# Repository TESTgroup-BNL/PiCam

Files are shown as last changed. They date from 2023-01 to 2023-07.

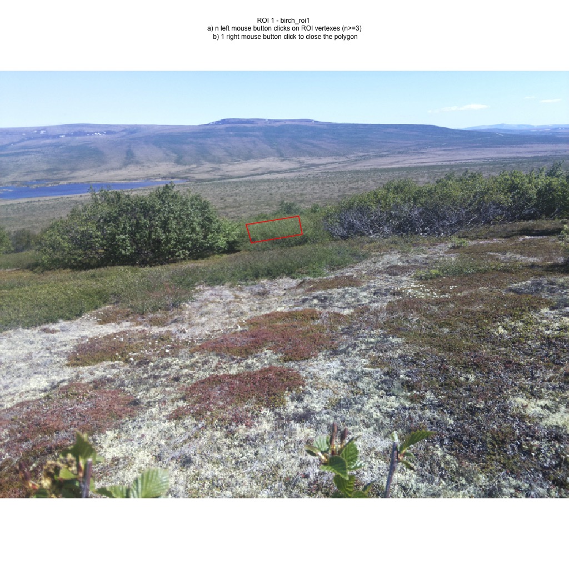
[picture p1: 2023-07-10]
Examples/Arctic_vegetation_phenology/pheno_results/roi/birch_roi1/spring/ROI1_birch_roi1.jpg

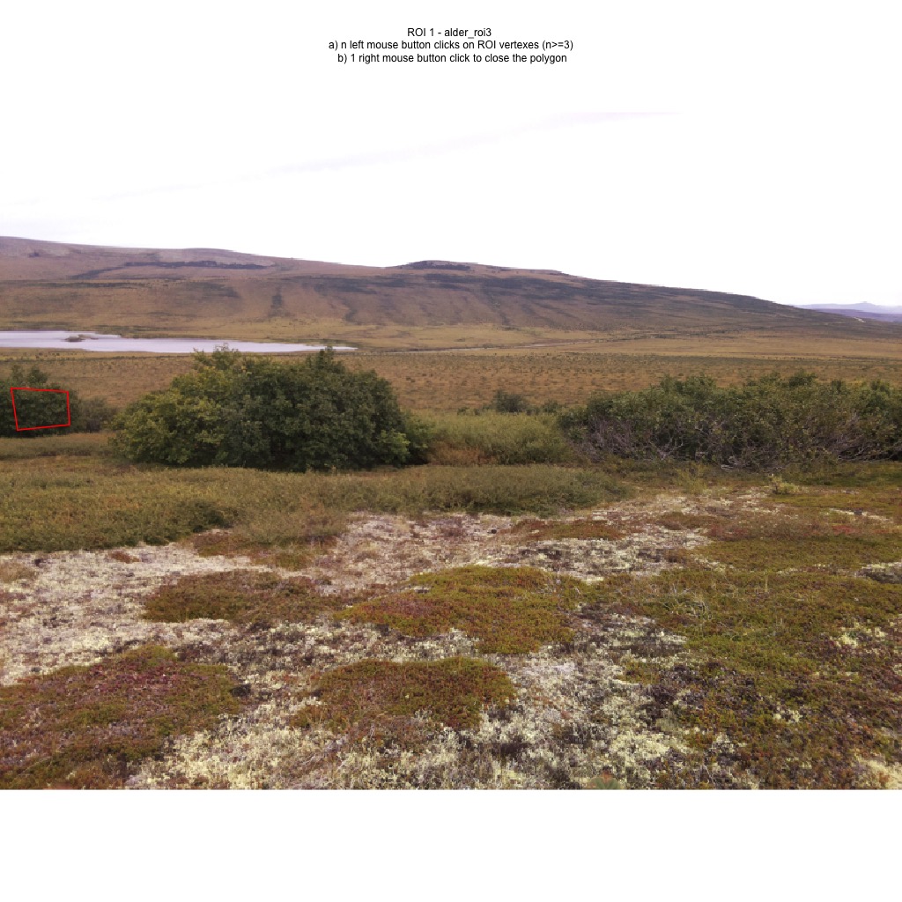
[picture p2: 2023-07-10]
Examples/Arctic_vegetation_phenology/pheno_results/roi/alder_roi3/fall/ROI1_alder_roi3.jpg

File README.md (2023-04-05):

### Source code citation: <br>


## Backgound
PiCAM is a custom-grade phenocam system designed by the [Terrestrial Ecosystem Science & Technology group](https://www.bnl.gov/envsci/testgroup/) at Brookhaven National Laboratory. The PiCAM has the advantage of being compact, low power cost, and lightweight, particularly suitable for Arctic environments. It was desinged to operate for at least a fiscal year (6 images per day) with three AA lithium batteries. Given its compact and light-weight feature, PiCAM can be deployed on small hosts (e.g., stakes), addressing the challenges of deploying heavy infrastructure commonly needed for commercial phenocams.

#### Below, we describe the parts, assemble, and basic operation of PiCAMs. Please also refer to Yang et al., (submitted to MEE) for more detailed technical description of the PiCAM and example applications in Arctic field sites. 

## 1. Parts for PiCAM
#### 2.1. Sensor Suite
* Camera (Raspberry Pi Camera v2; Raspberry Pi Foundation). Example source: https://www.raspberrypi.com/products/camera-module-v2/
* Camera cable (FFC Ribbon Cable; Generic). Example source: https://www.amazon.com/dp/B0716TB6X3/ref=twister_B08NTCX71W?_encoding=UTF8&psc=1
* GPS module (MINI GPS PA1010D STEMMA QT; Adafruit). Example source: https://www.digikey.com/en/products/detail/adafruit-industries-llc/4415/10709724
* GPS cable (FLEXIBLE QWIIC CABLE - 500MM; Sparkfun). Example source: https://www.digikey.com/en/products/detail/sparkfun-electronics/PRT-17257/13629026
#### 2.2. Central Control
* Supervisory controller (nrf52840; Nordic). Example source: https://www.digikey.com/en/products/detail/nordic-semiconductor-asa/NRF52840-DONGLE/9491124
* Camera controller (Raspberry Pi Zero; Raspberry Pi Foundation). Example source: https://www.raspberrypi.com/products/raspberry-pi-zero/
* Power Switch/Driver (TPS2080DR; Texas Instruments). Example source: https://www.digikey.com/en/products/detail/texas-instruments/TPS2080DR/1670863?s=N4IgTCBcDa4JwDYC0BmOKCsyCMSByAIiALoC%2BQA
#### 2.3. Power Supply
* Lithium Iron AA (Energizer; Part number: L91). Example source: https://www.energizer.com/batteries/energizer-ultimate-lithium-batteries
#### 2.4. Other Accessories
* Case (Flashlight; Fulton Industries). Example source: https://www.armynavysales.com/angle-head-flashlight-mx-991-u-me124-558.html
* Memory card (32GB Micro SD Card; Samsung). Users can choose the size depend on need
* SOIC-8 to DIP Breakout (BOB-13655; Sparkfun). Example source: https://www.digikey.com/en/products/detail/sparkfun-electronics/BOB-13655/5528943?s=N4IgTCBcDaIIwFYBsAOAtHOYDMaByAIiALoC%2BQA
* SWD Connector (10-pin 0.5mm; Samtec Inc.). Example source: https://www.digikey.com/en/products/detail/samtec-inc/SHF-105-01-F-D-SM/8410395

## 2. PiCAM Assembly, Programming, and Operation Guidance
A step-by-step instruction on how to assemble, program, and operate a PiCAM can be found at: https://github.com/TESTgroup-BNL/PiCam/wiki. Note that the assemble needed 3-D printed cases for housing the parts inside a Flashlight case. The design of these 3-D printed cases can be found at: https://github.com/TESTgroup-BNL/PiCam/tree/main/CAD. This guidance also include detailed instructions on how to program a PiCAM after assembly, as well how to operate a PiCAM using externel cell phone or latlop devices.

## Other Resources:
Adafruit nRF platform wrapper: https://github.com/dmpolukhin/Adafruit_nRF52_Arduino/tree/master/cores/nRF5

## Point of Contact:
Shawn Serbin: sserbin@bnl.gov Andrew Mcmahon: amcmahon@bnl.gov Daryl Yang: dediyang@bnl.gov Jeremiah Anderson: jeanderson@bnl.gov Wouter Hantson: wouter.hantson@umaine.edu

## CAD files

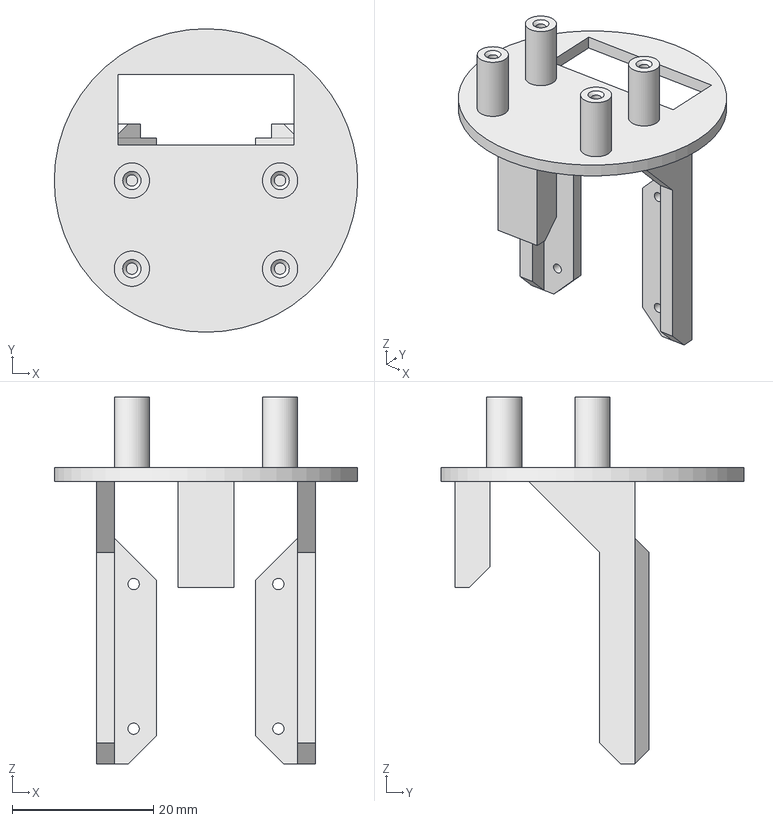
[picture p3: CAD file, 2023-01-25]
CAD/cam_holder_v2c.FCStd
43.0 x 43.0 x 52.0 mm

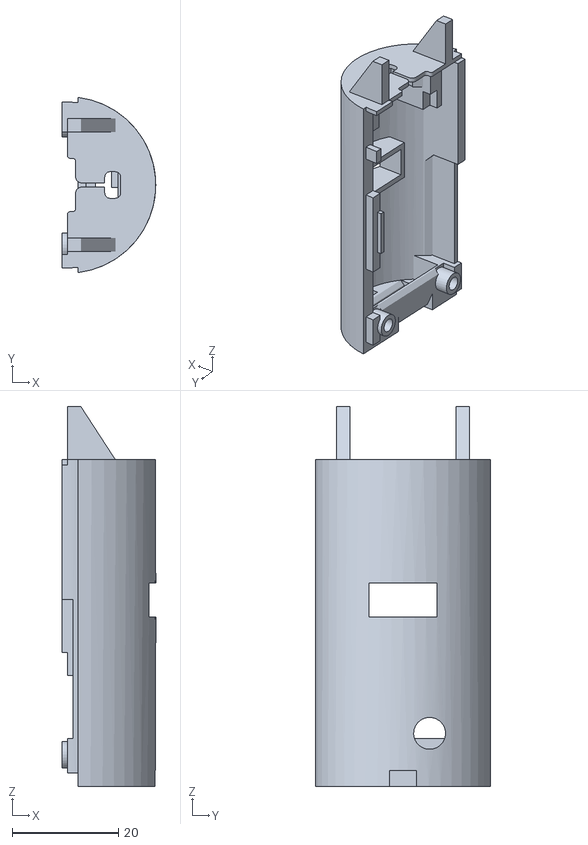
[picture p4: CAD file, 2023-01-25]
CAD/D-cell_nrf_Side_v11.stl
17.6 x 33.0 x 71.5

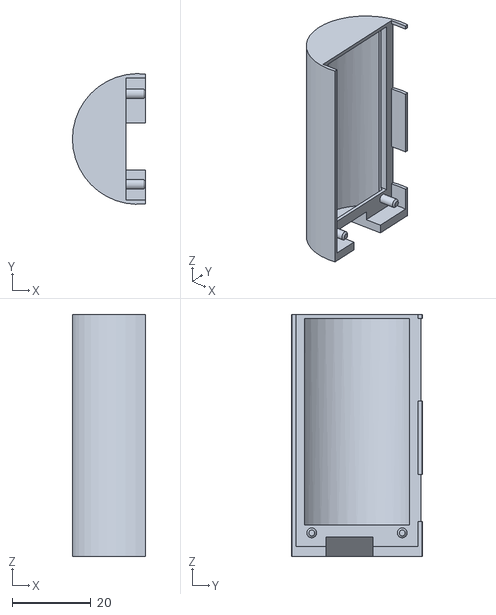
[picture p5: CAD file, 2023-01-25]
CAD/D-cell_Pi_Side_v11.stl
18.6 x 33.2 x 61.5

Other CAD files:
CAD/cam_gps_holder_v2c.stl

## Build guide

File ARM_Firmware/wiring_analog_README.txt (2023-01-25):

"wiring_analog.h" and "wiring_analog_nRF52.c" should go in the cores\nRF5 directory of the "Arduino Core for Adafruit Bluefruit nRF52 Boards" to support battery voltage reading.

Note that a fork of Adafruit package created by dmpolukhin is used for PCA10059 (nrf52840 Dongle) support.  This is configured in platformio.ini, noted here just for reference.

platform = https://github.com/dmpolukhin/platform-nordicnrf52.git
board = nordic_nrf52840_dongle
platform_packages = framework-arduinoadafruitnrf52@https://github.com/dmpolukhin/Adafruit_nRF52_Arduino.git

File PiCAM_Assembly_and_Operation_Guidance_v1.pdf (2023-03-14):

A Guidance for Assembling, Programming, and Operating the Power interval Camera [and sensor] Automation Module (PiCAM)

This document provides step-by-step guidance on how to assemble, program, and operate a Power interval Camera [and sensor] Automation Module (PiCAM) designed by the Terrestrial Ecosystem Science & Technology (TEST) Group at Brookhaven National Laboratory. This guidance is provided in alignment with a Wikipedia version that can be found on PiCAM GitHub: https://github.com/TESTgroup-BNL/PiCam/wiki. (https://github.com/TESTgroup-BNL/PiCam/wiki) For any questions you have regarding this guidance, please contact:

Andrew McMahon (amcmahon@bnl.gov), Daryl Yang (dediyang@bnl.gov), Jeremiah Anderson (jeanderson@bnl.gov), Shawn Serbin (sserbin@bnl.gov)

A. How to Assemble a PiCAM
1. Prepare power distribution board.
a. Attach TPS2080 to the breakout board.

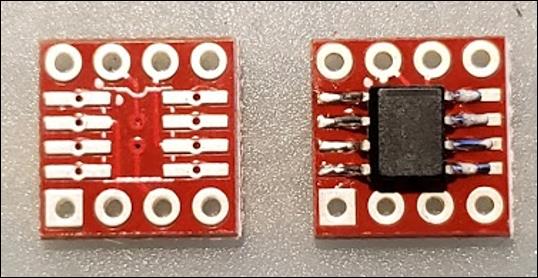
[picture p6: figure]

b. Cut trace to pad 8.

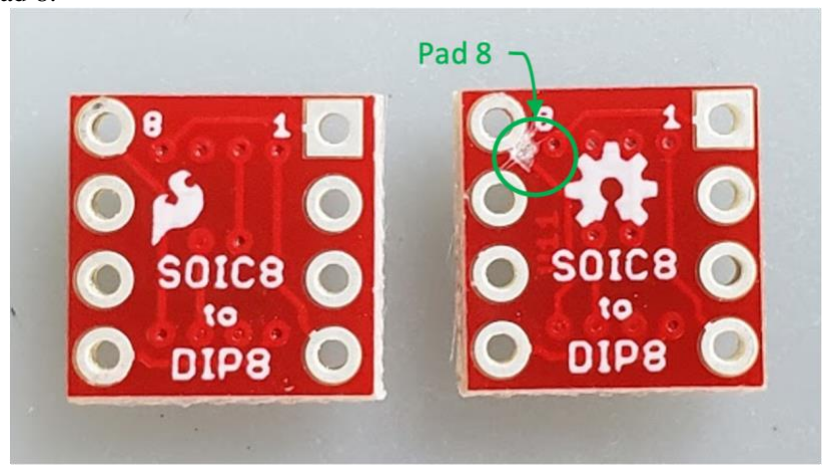
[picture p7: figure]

c. Attach MCP1700 (3.3V regulator). Leave VOUT pin long to attach I²C (GPS) power wire.

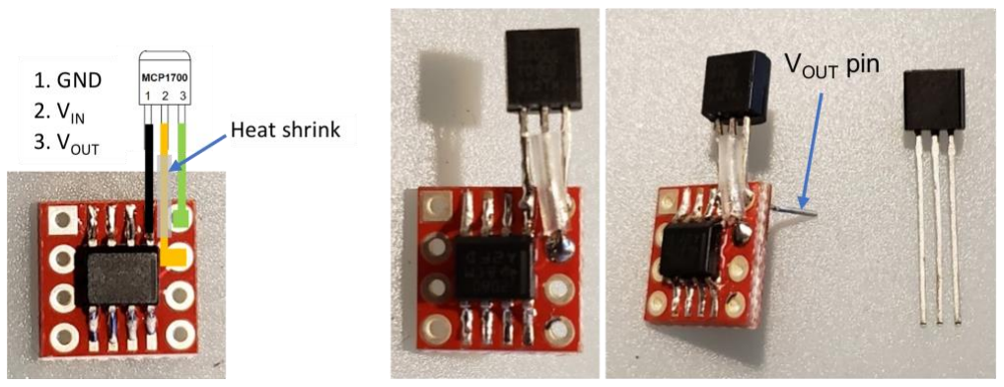
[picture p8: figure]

d. Attach the battery connector. If possible, pull about ½” of bare wire through the board, which will be used to attach to the USB pads on the Nordic dongle. The ground should go through from the chip side on pad 1 and the positive wire should be looped from the bottom through holes 2 and 3 and back down, so that both wires extend out of the bottom of the board.

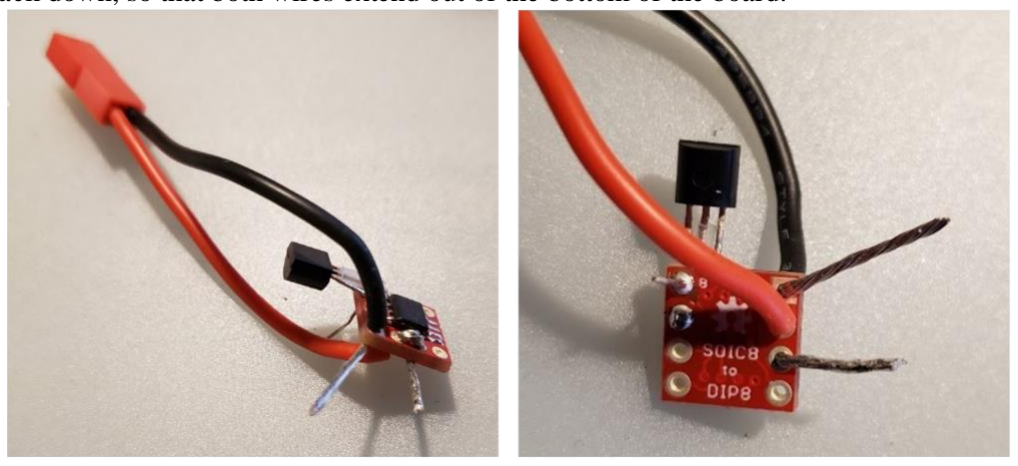
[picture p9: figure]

e. Connect the Pi and I²C power wires; The Pi positive connects to pad 6 and the I²C positive to pad 7, while both ground simply connect to the extended ground wire.

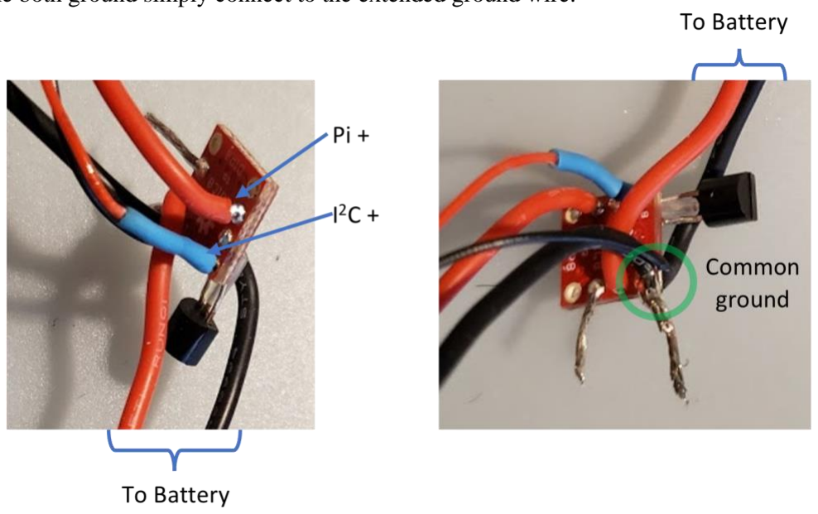
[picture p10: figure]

2. Attach J-link header to the Nordic nrf52840 dongle.

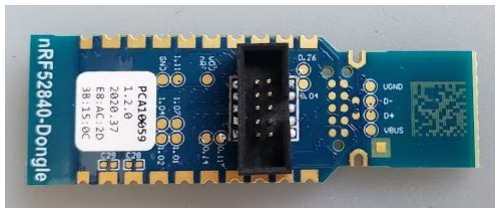
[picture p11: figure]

3. Attach power board to the Nordic dongle.
a. Connect V+ and ground to the USB pads. Note for reference that the positive pad has the square test point next to it.

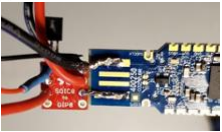
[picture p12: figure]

b. Connect the control lines from the power board to the dongle: Pad 4 to pin 0.20 and Pad 5 to 0.17.

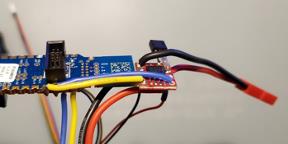
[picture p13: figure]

4. Connect serial lines for the Pi to the dongle on 0.13 (yellow) and 0.15 (blue) and I²C lines on 0.29 (blue) and 0.31 (yellow).

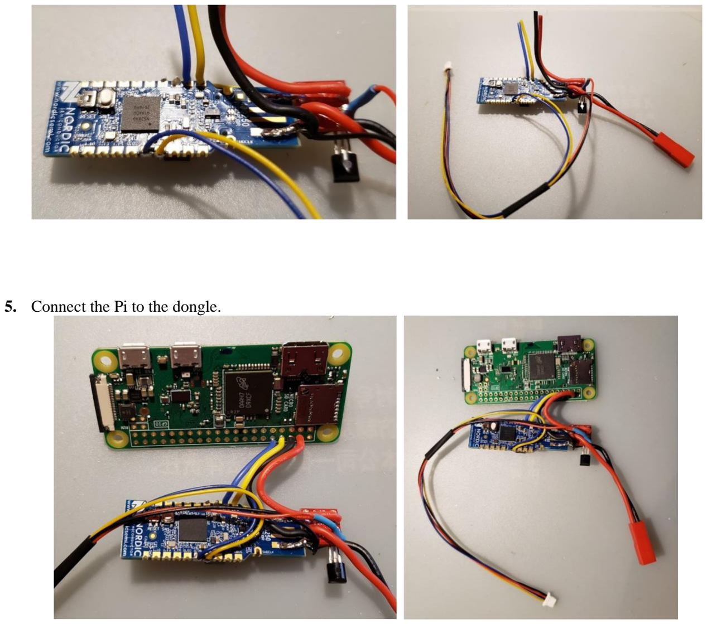
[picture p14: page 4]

5. Connect the Pi to the dongle.

### 6. Attach connector to battery holder. (Do NOT solder it with batteries in it.)

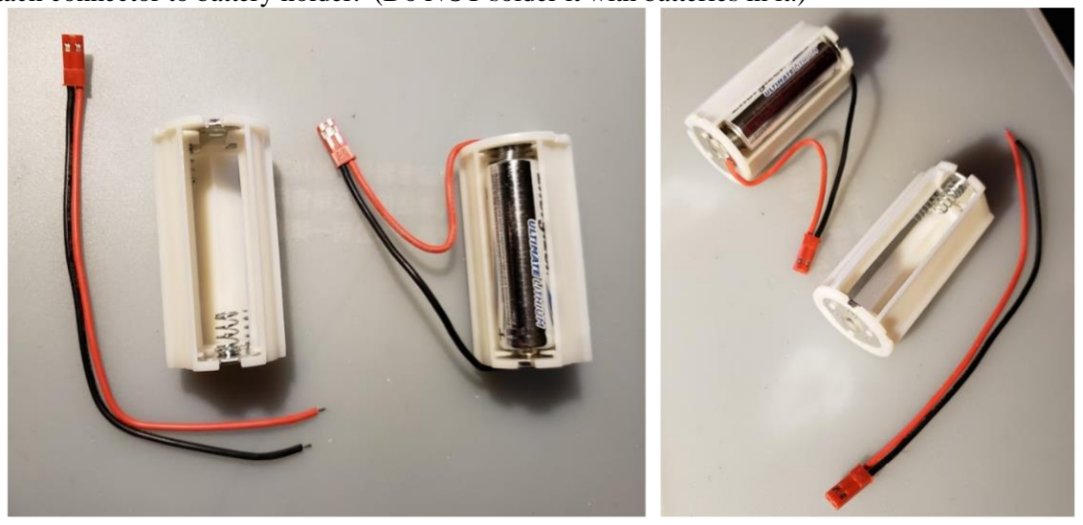
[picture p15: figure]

NOTE: This is the last of the soldering.

7. Print the “D-Cell” case and cam/GPS mount. (Pi-side of D-shell and partial cam/gps mount shown.)

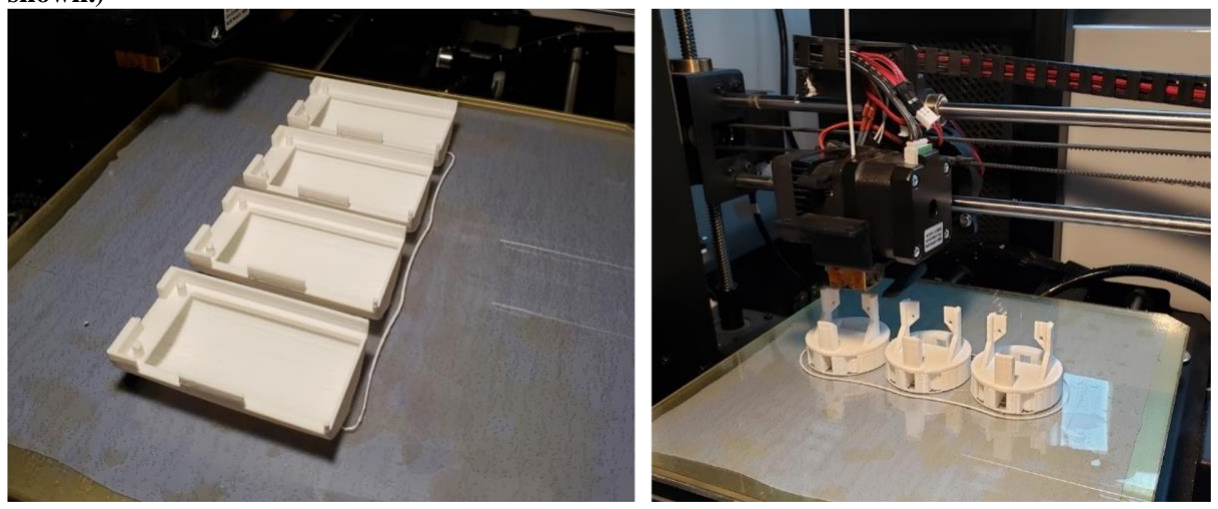
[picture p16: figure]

### 8. Put the dongle and Pi into the D-cell case:

a. Feed the battery connector through the bottom hole and tuck the nrf52840 dongle into the half D-cell. The power/regulator board should be on the bottom, tucked underneath the overhang, with the battery wire running just above the regulator through the thinner section of the bottom opening. Tuck the I²C cable behind the dongle as it is moved into place.
b. Gently, push the dongle down until the J-link connector can slide into the opening in the side of the case. It should pop in without much force; be careful not to crush the power board/regulator. Once the connector is in place, push down on the end of the dongle at the top of the case (where it says “Nordic”) to snap it into place.
c. Snap the Pi into the other half of the case. It needs to go in flat to avoid catching on the edges. If it is not sitting flush, try to realign it rather than using more force.

d. Finally, snap the two halves together, aligning the posts on the bottom.

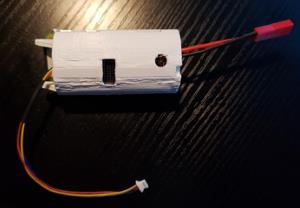
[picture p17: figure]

9. Attach the camera and GPS modules to the cam/GPS mount using M2 screws and washers on at the camera module. (The GPS module has pads very close to the screw holes, which could make washers risky depending on their diameter.)

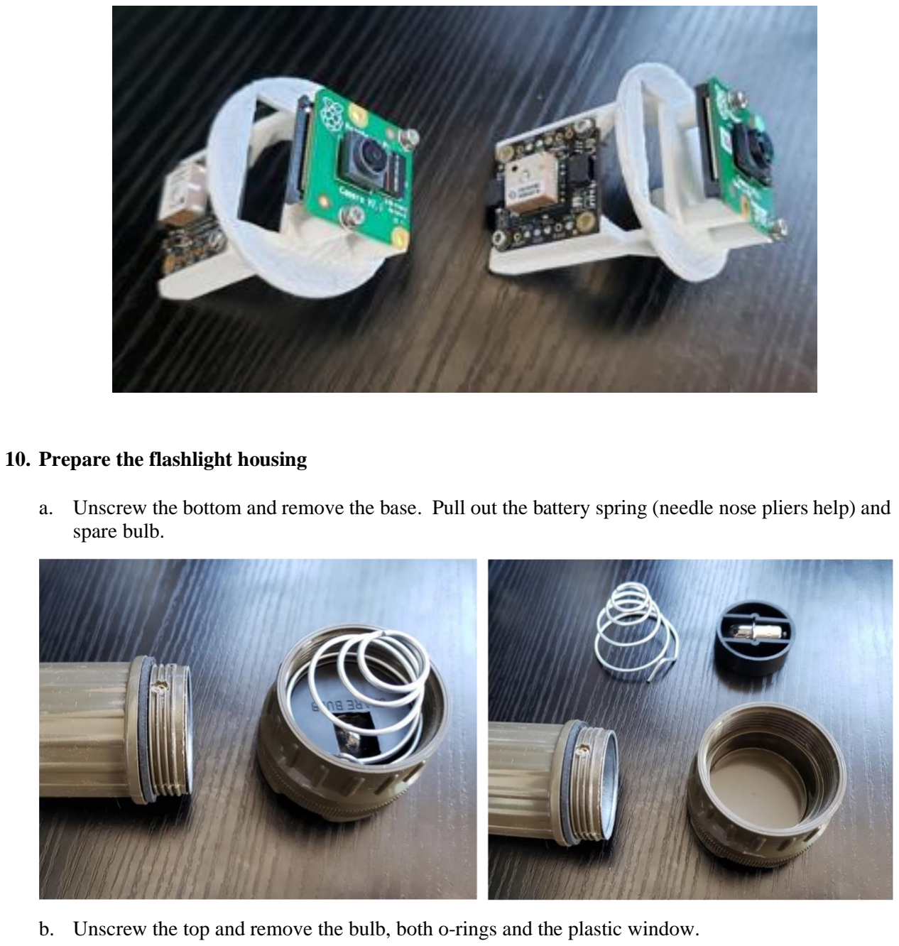
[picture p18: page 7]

### 10. Prepare the flashlight housing

a. Unscrew the bottom and remove the base. Pull out the battery spring (needle nose pliers help) and spare bulb.
b. Unscrew the top and remove the bulb, both o-rings and the plastic window.

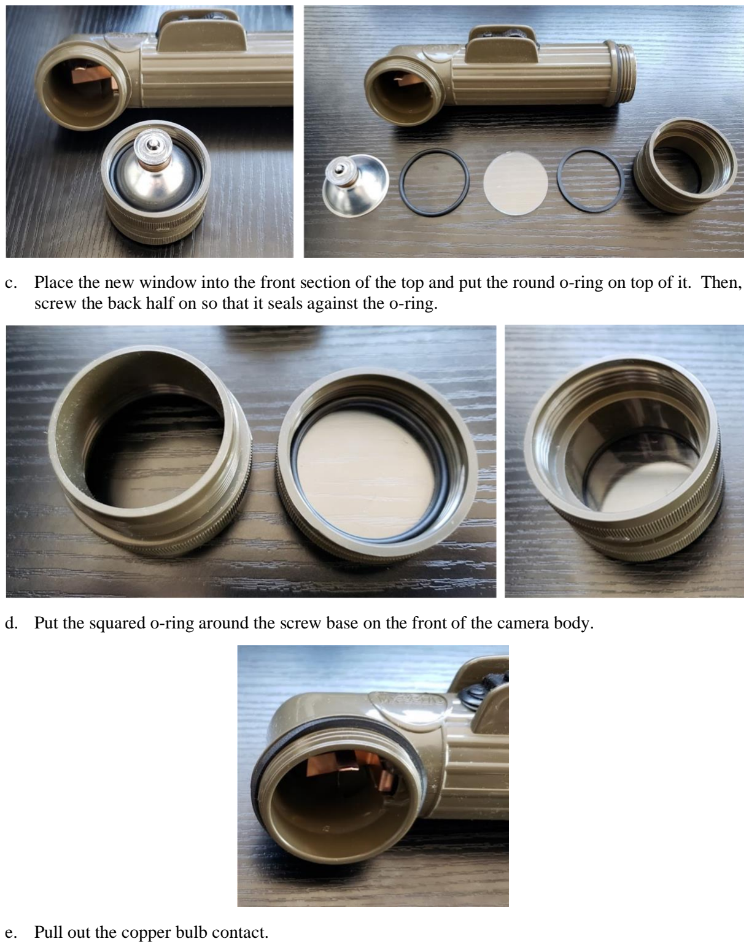
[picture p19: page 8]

c. Place the new window into the front section of the top and put the round o-ring on top of it. Then, screw the back half on so that it seals against the o-ring.
d. Put the squared o-ring around the screw base on the front of the camera body.
e. Pull out the copper bulb contact.

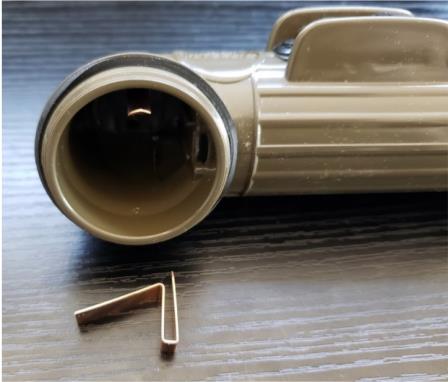
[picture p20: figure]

### 11. Insert the ribbon and I²C cables

Option 1: If the camera housing has a large enough opening, it may be possible to slide the camera ribbon cable through while attached to the Pi. In this case, it’s easy to feed the ribbon cable and I²C cable by taping them together. Having the I

2C cable attached also provides some tension to make positioning the ribbon cable easier.

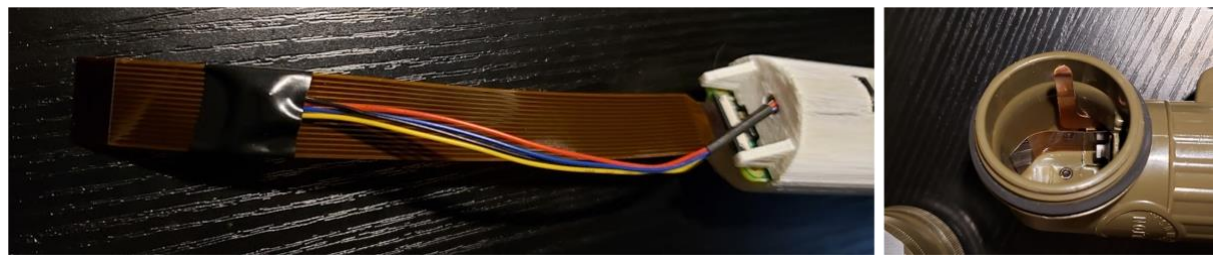
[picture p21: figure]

Option 2: If the opening is too narrow to easily slide the cable though, the ribbon cable can be pushed through from the top, then attached to the Pi.

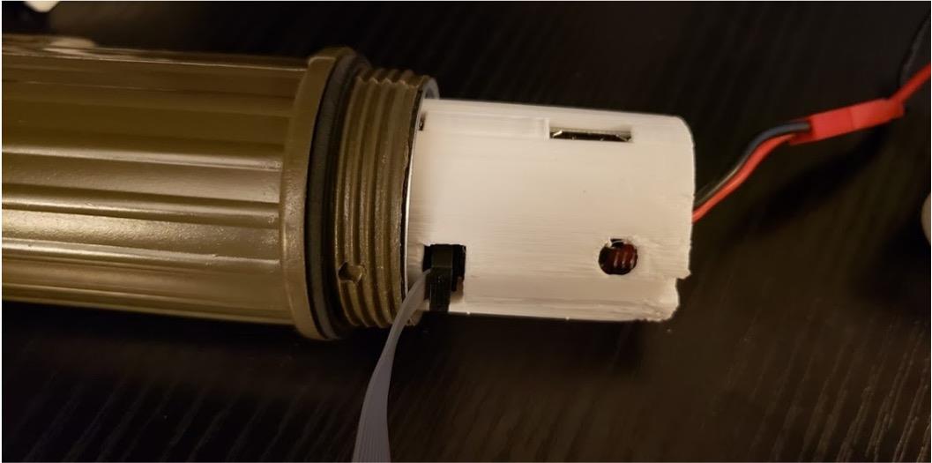
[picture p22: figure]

Note: This is the last opportunity to access the J-link connector and upload firmware without disconnecting the ribbon and I²C cables!

12. Slide the D-cell case into the camera body. Gently “pull” (more so allow them to move freely) the two cables from the front of the camera to ensure that they do not get tangled/crumpled above the D-cell case.

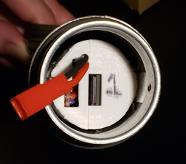
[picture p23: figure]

13. Attach the I2C cable to the GPS module and the ribbon cable to the camera module.

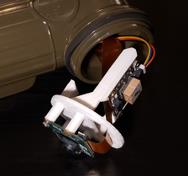
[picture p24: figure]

14. Insert the camera/GPS assembly. Place a desiccant packet under the GPS module and slide the assembly into place. (The bottom is keyed to lock into the bottom of the body opening and keep the assembly straight.) Then, screw on the front.

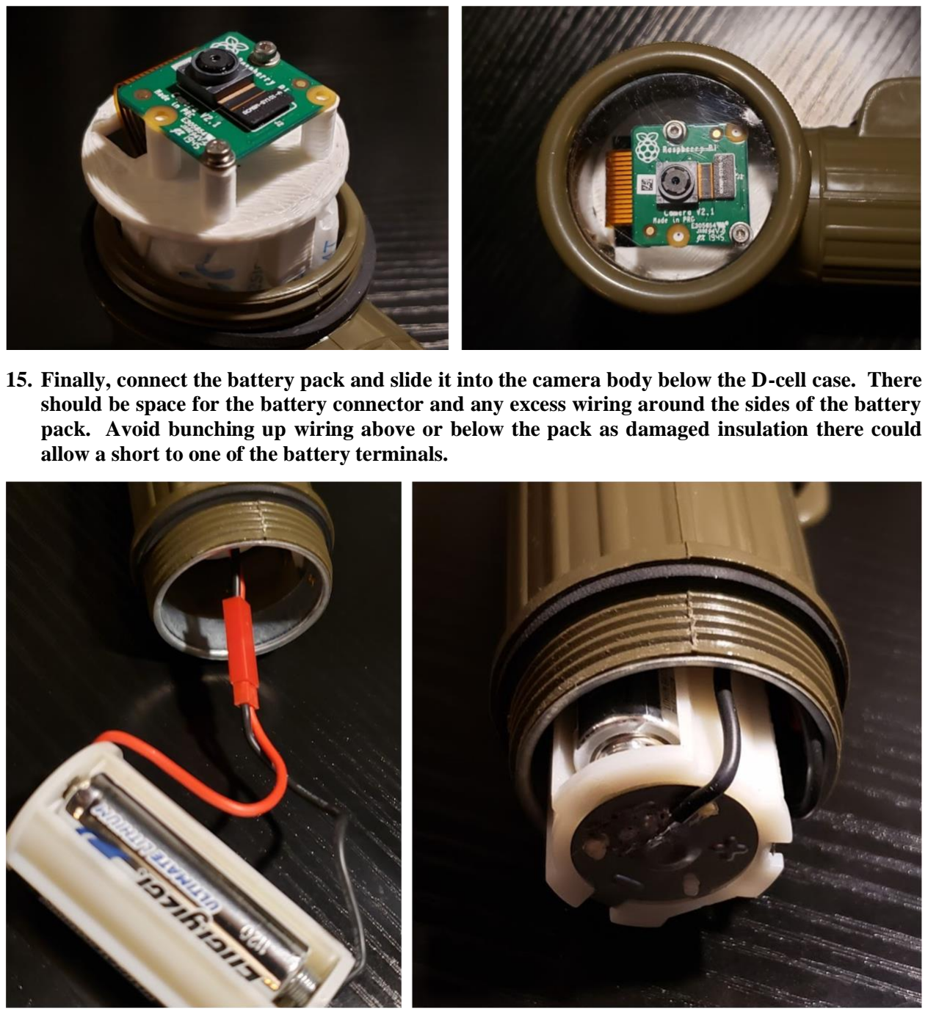
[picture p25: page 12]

15. Finally, connect the battery pack and slide it into the camera body below the D-cell case. There should be space for the battery connector and any excess wiring around the sides of the battery pack. Avoid bunching up wiring above or below the pack as damaged insulation there could allow a short to one of the battery terminals.

B. How to Program a PiCAM
1. Download the nRF firmware hex file (SoftDevice_S140_6_1_1-App_2_1_1.hex) from PiCAM GitHub (https://github.com/TESTgroup-BNL/PiCam/tree/main/ARM_Firmware)
2. Download nRF Connect for Desktop (https://www.nordicsemi.com/Products/Development-tools/nrf-connect-for-desktop/download) (https://www.nordicsemi.com/Products/Development-tools/nrf-connect-for-desktop/download) and install it on a PC or Mac.
3. Open nRF Connect, and install Programmer. Once installed, open Programmer.

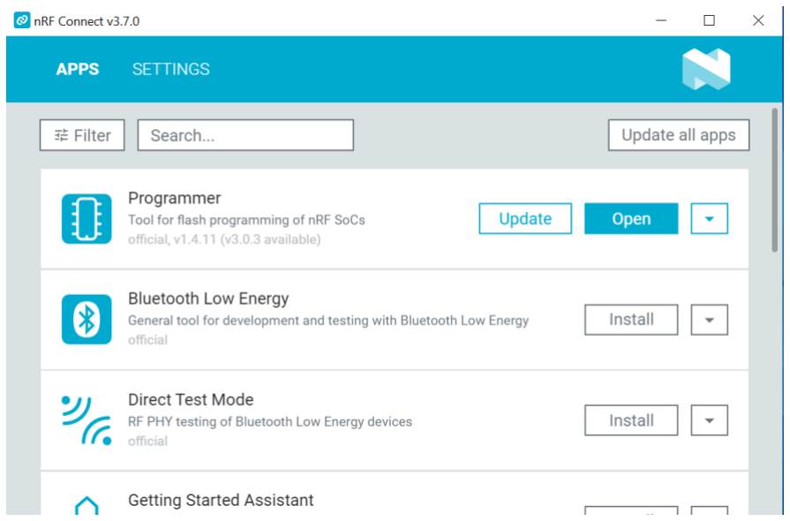
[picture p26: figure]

4. Connect the PiCAM to your PC or MacOS through a USB port using J-Link GTAG/SWD debugger (https://www.segger.com/products/debug-probes/j-link/models/j-link-edu-mini/).
5. In nRF Connect, click “SELECT DEVICE”, and choose your PiCAM from the drop-down list. Once your PiCAM is connected, its memory layout will be shown in the right-hand panel.

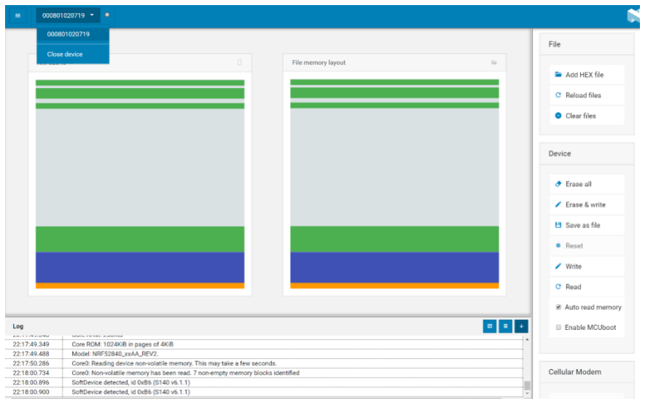
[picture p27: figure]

6. In nRF, click on ‘Add File’ and locate your .hex file downloaded from PiCAM GitHub. Or you can directly drag and drop your .hex file to the left-hand panel “File memory layout”.

7. Once both the ‘File memory layout” and “Device memory layout” are loaded, click “Erase and write” to overwrite the Device memory using .hex file. Once this step is completed, you will see a printout in the log like below.

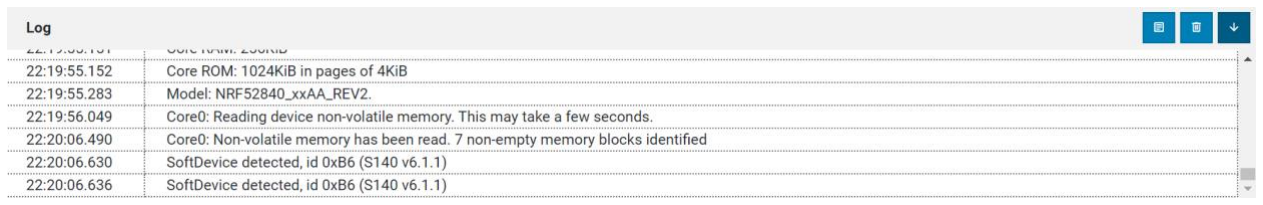
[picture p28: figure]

8. Disconnect your PiCAM from nRF Connect.
9. Download Pi Zero firmware folder from GitHub:

https://github.com/TESTgroup-BNL/PiCam/tree/main/Pi_Firmware

10. Prepare an empty microSD card and format it.
11. Copy and paste the Pi Zero firmware into the main folder on your microSD card.
12. Open the ‘cam_cfg.txt” file and modify image capture frequency, time zone (UTM+), and other necessary parameters based on user need.
13. Plug the SD card into Pi Zero

C. First Power Up and Operation Loop

When first powered on, the PiCAM will first turn on the nRF supervisory microcontroller. The nRF will then attempt to:

1. Power on the Pi Zero,
2. Read the configuration file stored on microSD card,
3. Power on the Pi Camera module and take a picture,
4. Power on the GPS module and get a GPS lock for time and location (the GPS module has a green LED that is visible through the camera window). This step might take one to a couple of minutes to complete.

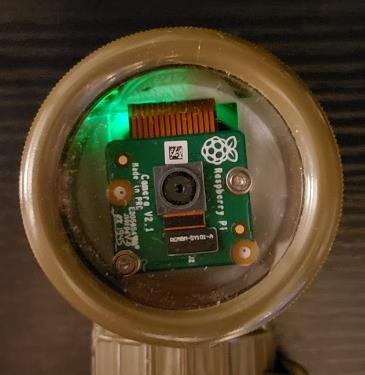
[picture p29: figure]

At this point, the camera will show up as a Bluetooth device and can be scanned by any device with Bluetooth Lower Energy (BLE) capacity, but will not yet show accurate information (ID, date, time) in the advertising string. Once a GPS lock is acquired (or times out), the camera will enter “normal” operation mode, where the scheduled event loop takes over. Once in the main loop, the Bluetooth advertising information will be updated every 5 seconds, and it will respond normally to Bluetooth connections.

Normal Operation Loop

Once operating, the PiCAM will capture images at the interval specified in the configuration file (https://github.com/TESTgroup-BNL/PiCam/blob/main/Pi_Firmware/cam_cfg.txt). The image interval is synchronized to hours/minutes, so that offsets are evenly spaced throughout the day starting from 12 AM, rather than a timed interval between images. For example, if a camera is set to a 15-minute interval and powered on at 11:52 AM, its first image will be at 12:00 PM and the next at 12:15 PM, rather than a direct offset of 15 minutes from power on, which would give uneven times of 12:07 PM, 12:22 PM.

Turning on/off: The camera starts when the batteries are connected and stops when they are disconnected; there is no other start/stop mechanism. Disconnecting power while an image is being saved should be avoided as much as possible as this could cause SD card corruption. (Users can look at the UART terminal or dashboard to check if an image is currently being captured). There is no other “safe power down” requirements.

D. Bluetooth Communication with External Devices

The Bluetooth function of a PiCAM stays on at all times and can provide information in a variety of ways:

- The Advertising String
An advertising string is visible without connecting or any specific software. Any device (phone, computer, etc.) that can scan for Bluetooth Low Energy (BLE) devices should be able to “see” it. The format of the advertising string is shown below:

Format: PiCam <ID> <Battery Level as %> <images captured in current run> <date> <time> Example: PiCam001 95 0512 08/07 13:08

- Serial UART Connection
This connection provides a terminal-like text interface. The Adafruit Bluefruit Connect app works great for this and is available for both Android (https://play.google.com/store/apps/details?id=com.adafruit.bluefruit.le.connect) and iOS. (https://apps.apple.com/us/app/adafruit-bluefruit-le-connect/id830125974)

Usage: Once connected to a PiCAM, the app will receive periodic strings from the camera with basic status information. Sending any character will trigger the app to print out a menu with several options:

'c': Print cfg
'g': Get GPS fix
'i': Capture image now
'r': Reload cfg
't [YYYY,MM,DD,hh,mm,ss]': Set time

Sending a specified character listed above will trigger the command. If users do not wish to print the menu, sending a double character of any command above will execute it without displaying the menu. For example, to quickly trigger getting a GPS fix, sending ‘gg’ will immediately start that command.

- Web Dashboard
The web dashboard provides the most remote functionality including all the items from the UART menu as well as getting preview images and syncing time to the host. It displays the UART data as a text feed and additionally parses it to better display the data.
The dashboard utilizes Web Bluetooth, which is currently an experimental API but has reasonable support for Chrome (the progress of adoption can be checked here). (https://caniuse.com/web-bluetooth) Nevertheless, some bugs and changes should be expected as this continues to develop. The current site being used for testing is hosted at https://web-picam.glitch.me/, but should be cached offline for use in the field. Tip: Connecting can take 10-15 seconds; if the Bluetooth icon hasn’t appeared on the tab yet, clicking connect again sometimes does the trick. Other times it causes a disconnect or a “double connection” where everything is printed twice (though commands still work fine).

Preview image: When triggered, this powers up the Pi, captures a low-resolution image, and transfers it to the nrf52840, which finally transfers it to the dashboard. Transferring from the Pi to the nrf52840 can be very slow (it’s 230400 baud serial), so it may take 15-30 seconds even for a small image. The Bluetooth transfer is generally much faster, taking only a few seconds. Chrome can be picky about rendering the image once it’s received; if it isn’t displayed immediately, try opening/switching to a different tab and then back to force it to redraw.

Important: While connected to Bluetooth (UART or dashboard), the camera is consuming about 10 times as much power as in “normal” standby, so it is important to not stay connected indefinitely and to remember to disconnect! (If a connection is dropped by device moving out of range or interference, the camera will automatically drop the connection rather than being stuck in connected mode.)

E. Configuration File

Most aspects of the camera configuration are determined by the “cam_cfg.txt” file on the SD card. (If there is no file/SD card, the defaults will be used.) Each parameter should be on its own line in the format <Parameter> <Value> (one space between parameter and value). This file can include short comments after a parameter, separated by at least one space from the parameter value.

Parameter | Description | Default Value | Units | Format | Usable Range
ID | Arbitrary Camera ID | 0 | None | Unsigned Integer | 0-999
IMAGE_INTERVAL | Frequency to capture images | 30 | Minutes | Unsigned Integer | 1-1440
BLE_INTERVAL | Frequency to update advertising string | 1 | Minutes | Unsigned Integer | 1-1440
GPS_INTERVAL | Frequency to update GPS info (location and time) | 24 | Hours | Unsigned Integer | 1-720
CLK_SYNC_INT | Minimum time before next GPS clock sync | 60000 | Milliseconds | Unsigned Long | 1000-86400000
CLK_RESOLUTION | Main loop delay time; all other timers are checked at this interval. Significantly impacts battery life. | 5000 | Milliseconds | Unsigned Long | 1000-60000
PI_ON_TIMEOUT | Time to wait for communication from Pi after powering it on. | 10000 | Milliseconds | Unsigned Integer | 1000-60000
PI_SAVE_TIMEOUT | Time to wait for a saved image confirmation from Pi. Setting too low can cause corrupted images. | 30000 | Milliseconds | Unsigned Integer | 1000-60000
GPS_TIMEOUT | Time to wait for GPS fix | 120000 | Milliseconds | Unsigned Long | 1000-1800000
MAX_BATT_VOLTAGE | Maximum expected battery voltage. Used to scale battery %. | 5.2 | Volts | Float | 3.3-5.5
LOW_BATT_CUTOFF | Minimum battery voltage. Once the voltage falls below this threshold, the camera will no longer attempt to capture images. Also used to scale battery %. | 3.4 | Volts | Float | 1.2-MAX_ BATT_ VOLTAGE
TZ_OFFSET | Time offset from UTC | -5 | Hours | Signed Integer | -12-12

For most cases, a user should only need to change IMG_INTERVAL, GPS_INTERVAL, and TZ_OFFSET. Changing any parameter, especially CLK_RESOLTUION, IMG_INTERVAL and GPS_INTERVAL, can have a significant impact on battery life.

F. Image and Log Data

Images are saved to the SD card in the Pi. Each time the camera is powered on (or explicitly told to), it starts a new “run”. Each run has a numbered folder in the images folder. This prevents any accidental overwrites and a degree of metadata if clock information is missing or inaccurate. Images are named in the following format:

“img_<cam ID>_<cam MAC>_<date>_<time>.jpg”
(Files for preview images are saved with the prefix “prv”.)

Each time an image is saved, a CSV record is added to “log.txt” with the following fields: Example record: 00:00:15, 0\img_5_0C7732331A02_2021-04-15_142000.jpg, 5.18,0.00,40.748938,N,-73.942496,W,77.400002,6,1

Field | Description | Example
Time | Time since Pi powered on; NOT time of day. This is a useful diagnostic to determine how long it’s taking the Pi to capture and save images. A slow or corrupt SD card can cause very long save times, impacting battery life. | 00:00:15
Filename | Image filename. (“images” folder is implied as the root.) | 0\img_5_0C7732331A02_ 2021-04-15_142000.jpg
Battery Voltage | Battery voltage before Pi is powered on. | 5.18
Temperature | Internal temperature of nrf52840. Currently not implemented. | 0.00
Latitude | Latitude from last GPS fix. Note that the sign and direction (N/S) can be redundant. | 40.748938 N
Longitude | Longitude from last GPS fix. Note that the sign and direction (E/W) can be redundant. | -73.942496 W
Altitude | Altitude from last GPS fix. Note that it is possible to have a lat/long but no altitude because a 3D fix takes longer than a 2D fix. | 77.400002
Satellites | Satellites used for last GPS fix | 6
Fix Quality | GPS fix quality (0, 1, 2 = Invalid, GPS, DGPS). DGPS does not apply with the current hardware. | 1

The “images” folder and “log.txt” can be safely deleted at any time; they will be automatically recreated. However, the following files should always be present on the SD card and should not be modified (other than “cam_cfg.txt”):
bootcode.bin
cam_cfg.txt
config.txt
fixup.dat
fixup_x.dat
kernel.img
libraspistill.a
start.elf
start_x.elf

Other Tips/Notes:
- The SD card can be safely removed or inserted without powering down the camera provided it’s not actively trying to save an image. This allows checking data without restarting a run, but should still be done with caution.
- It is highly recommended to use tweezers to pull out the SD card.
The D-cell case containing the Pi and nrf52840 cannotslide out of the camera body with the camera and GPS modules connected. Trying to pull it will likely pull the ribbon cable out of the Pi, requiring the camera and GPS modules to be disconnected and removed, the cable reattached to the Pi, and then fed back through the body. (In other words, an annoying amount of work.)

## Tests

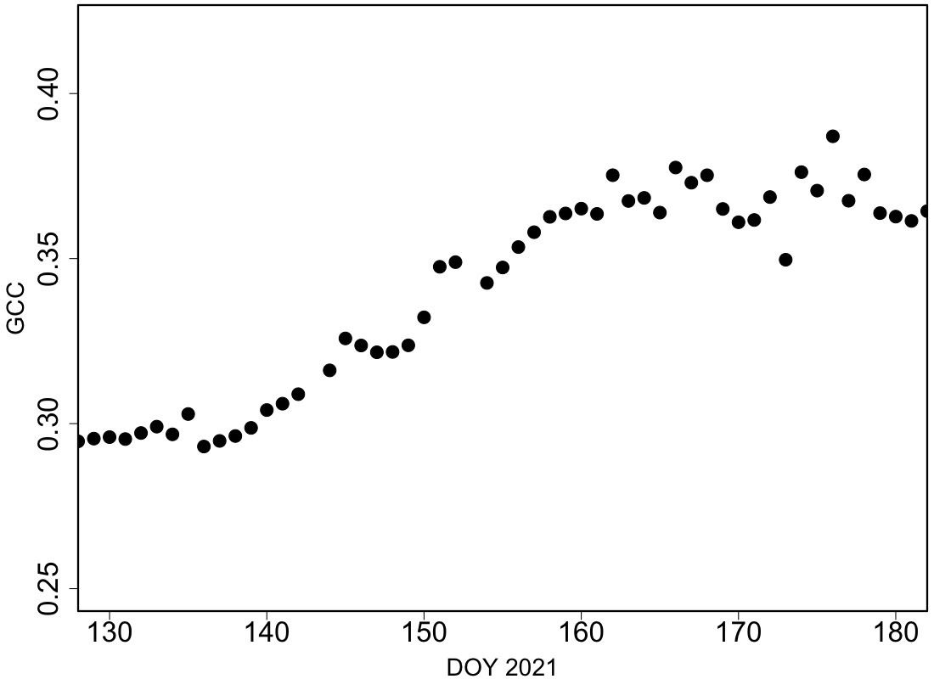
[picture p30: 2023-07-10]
Examples/Arctic_vegetation_phenology/pheno_results/roi/birch_roi2/spring/spring_gcc.png

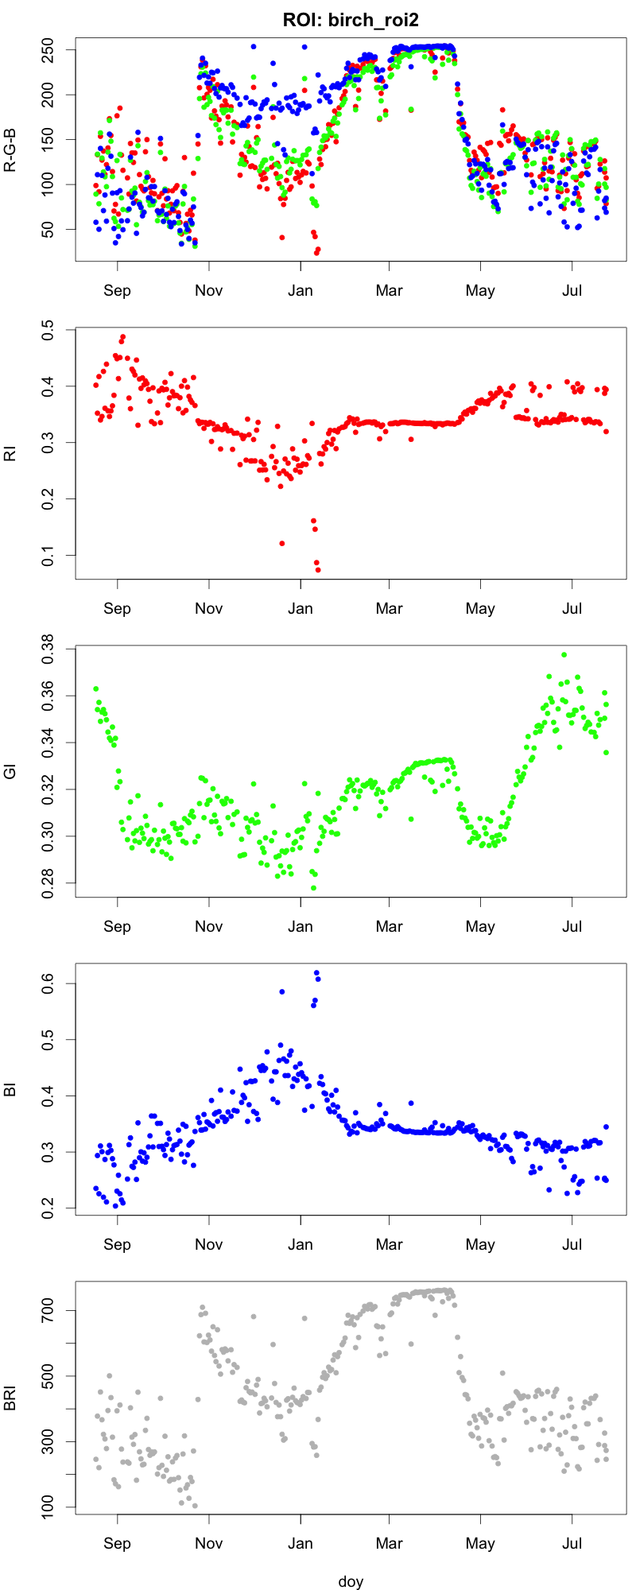
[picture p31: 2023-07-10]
Examples/Arctic_vegetation_phenology/pheno_results/roi/birch_roi2/fall/birch_roi2_roi_VI_plot.png

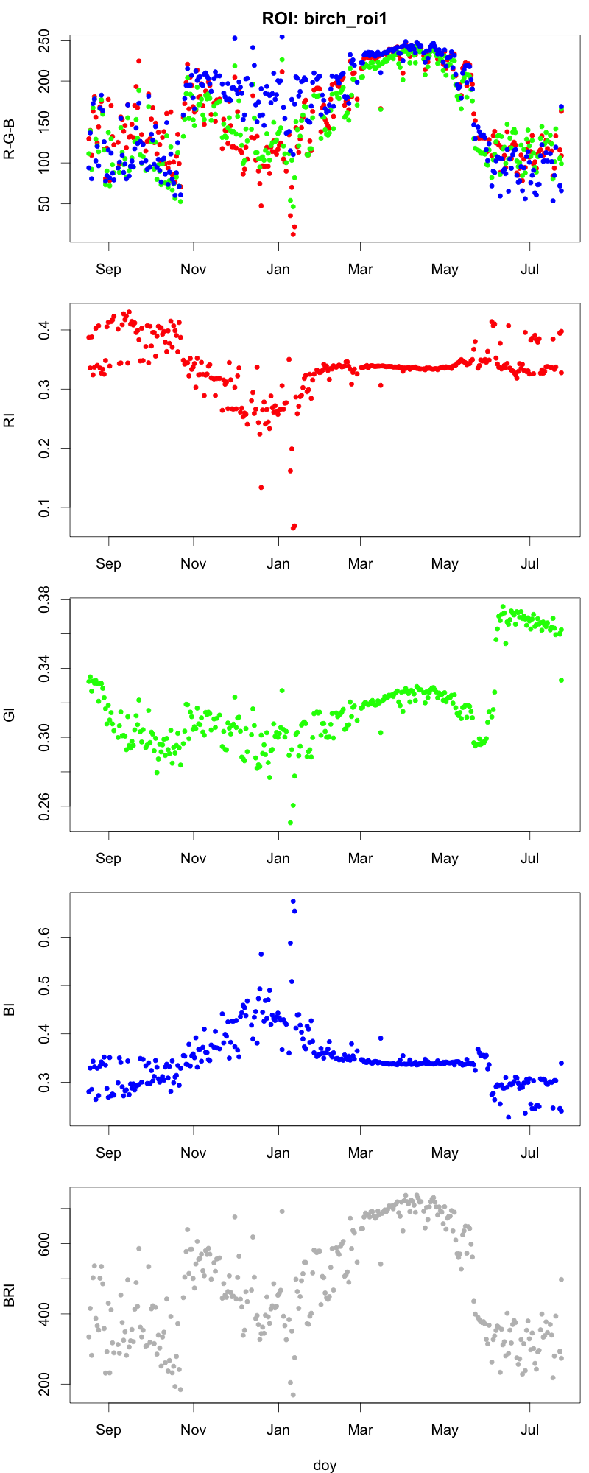
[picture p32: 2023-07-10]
Examples/Arctic_vegetation_phenology/pheno_results/roi/birch_roi1/spring/birch_roi1_roi_VI_plot.png

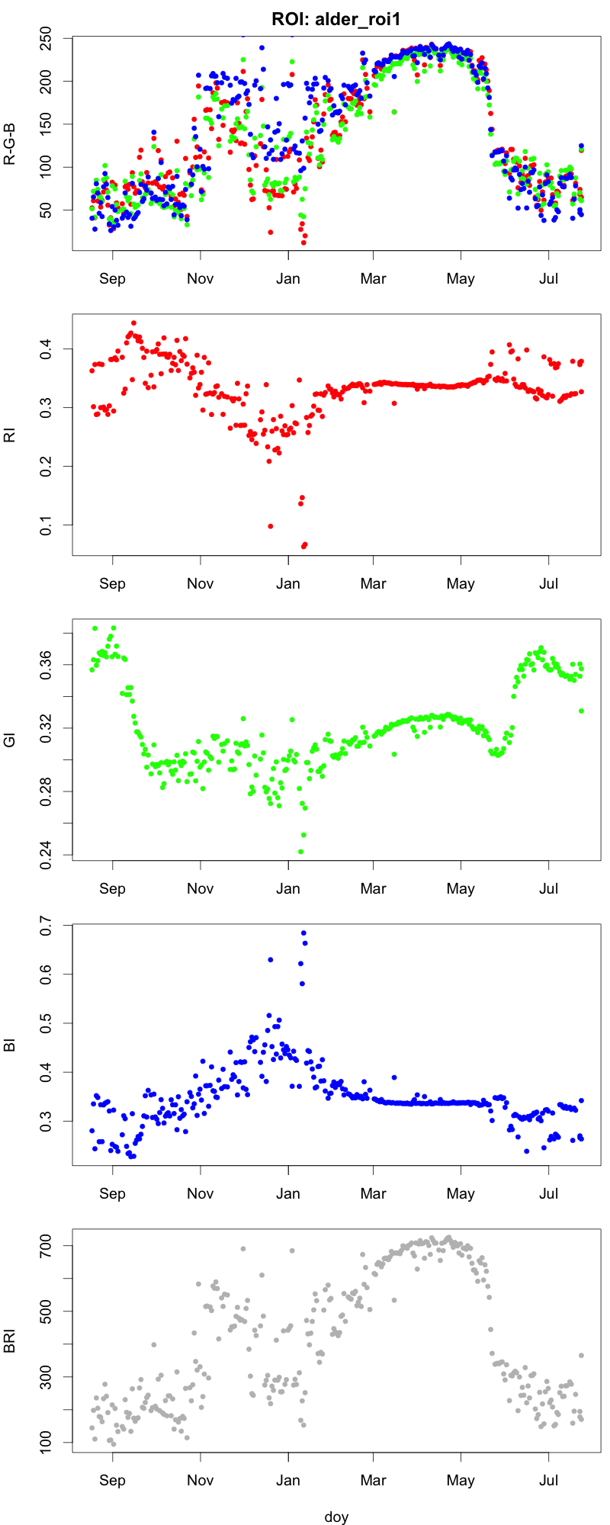
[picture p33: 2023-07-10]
Examples/Arctic_vegetation_phenology/pheno_results/roi/alder_roi1/fall/alder_roi1_roi_VI_plot.png

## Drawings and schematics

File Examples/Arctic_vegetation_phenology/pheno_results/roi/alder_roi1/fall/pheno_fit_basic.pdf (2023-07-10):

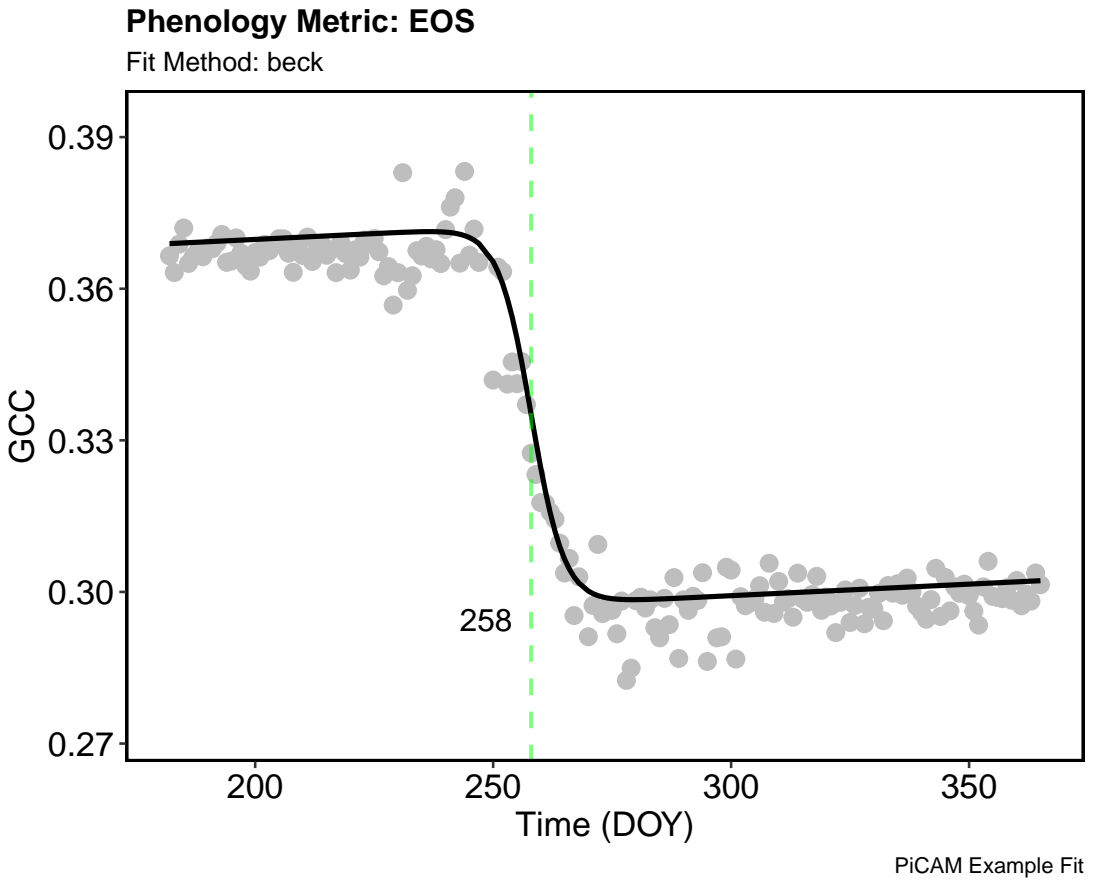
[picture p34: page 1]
Time (DOY); GCC

Phenology Metric: EOS
Fit Method: beck

PiCAM Example Fit

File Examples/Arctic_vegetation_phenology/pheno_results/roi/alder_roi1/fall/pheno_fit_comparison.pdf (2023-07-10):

0.005 | pop | eos | | pop | eos | sos | Greenup | | Senescence Maturity | Dormancy | | DD | RD

## TRS

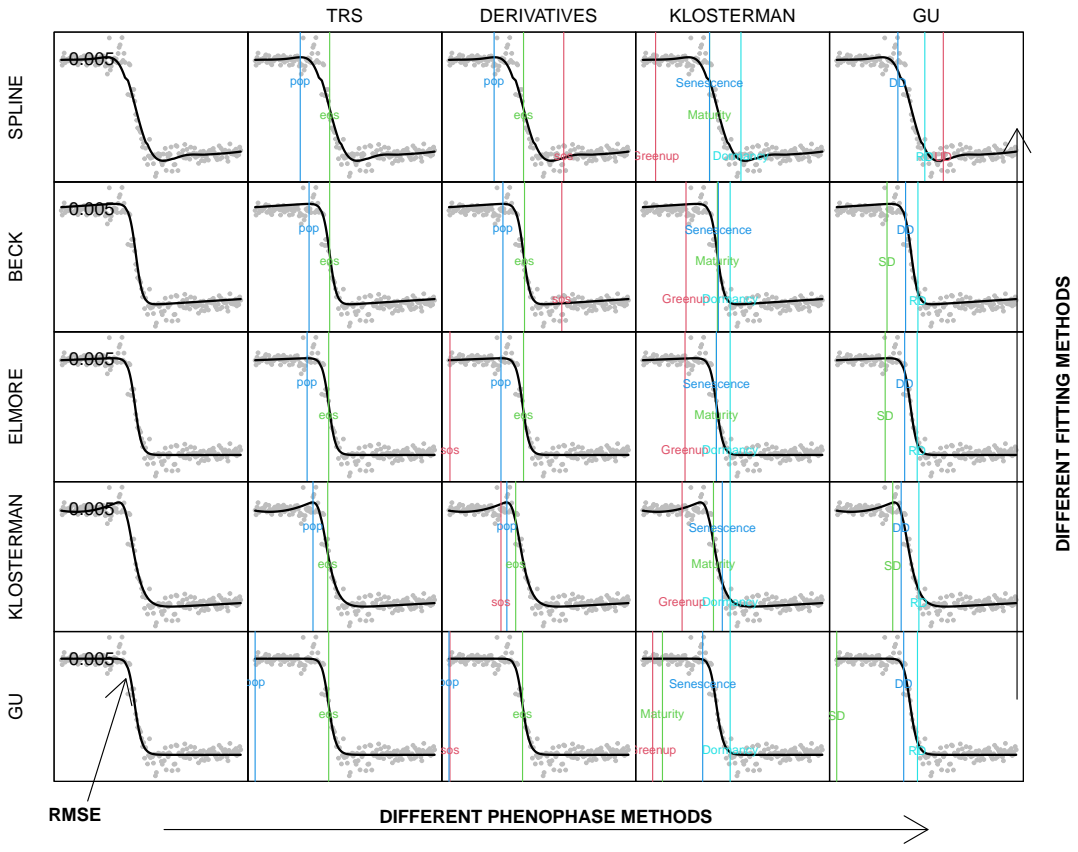
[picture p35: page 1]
x$data SPLINE; x$data; DERIVATIVES; KLOSTERMAN; BECK; ELMORE; x$data GU; RMSE

0.005 | pop | eos | | pop | eos | sos | | Greenup | Senescence Maturity Dormancy | | | SD | DD | RD

DIFFERENT FITTING METHODS

0.005 | pop | eos | | sos | pop | eos | | Greenup | Senescence Maturity Dormancy | | | SD | DD | RD

0.005 | pop | eos | | pop sos | eos | | Greenup | Senescence Maturity Dormancy | | | | SD | DD | RD

0.005 pop | | eos | pop | eos sos | Greenup | Maturity | | Senescence | Dormancy | | DD SD | RD

DIFFERENT PHENOPHASE METHODS

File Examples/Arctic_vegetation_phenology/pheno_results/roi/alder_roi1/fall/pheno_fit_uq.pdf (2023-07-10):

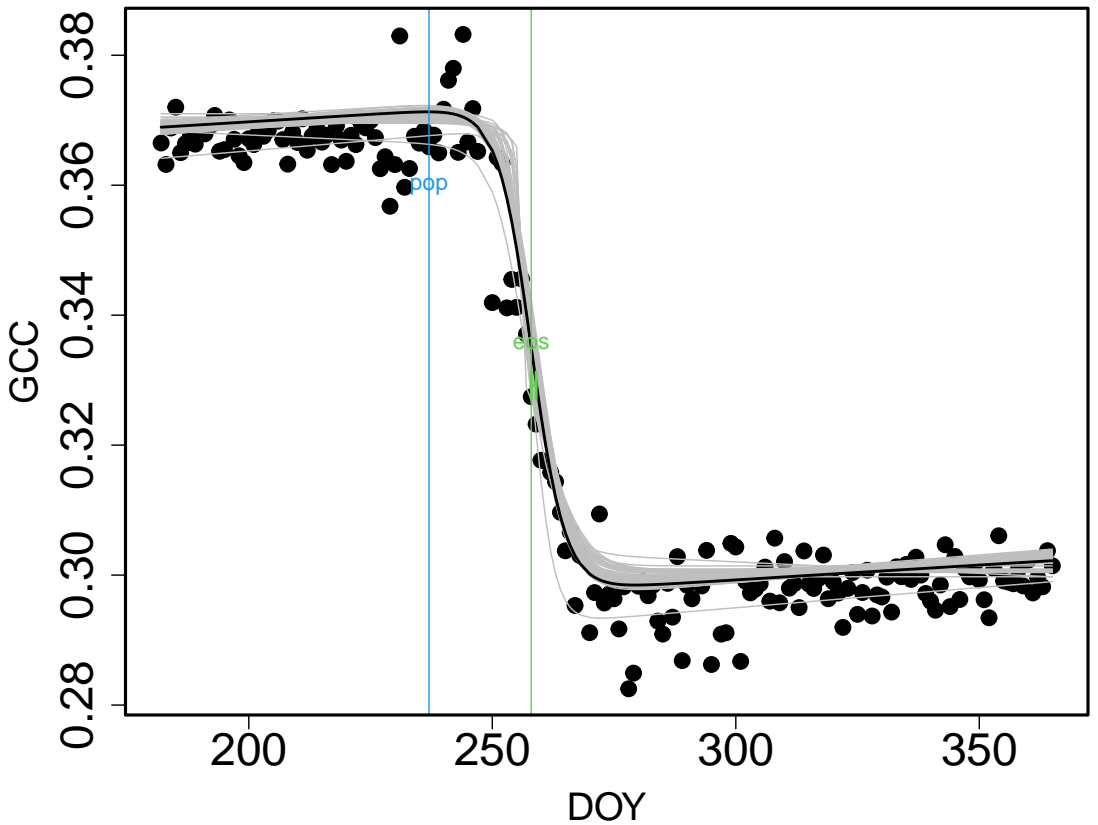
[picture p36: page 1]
DOY; GCC; eos; pop

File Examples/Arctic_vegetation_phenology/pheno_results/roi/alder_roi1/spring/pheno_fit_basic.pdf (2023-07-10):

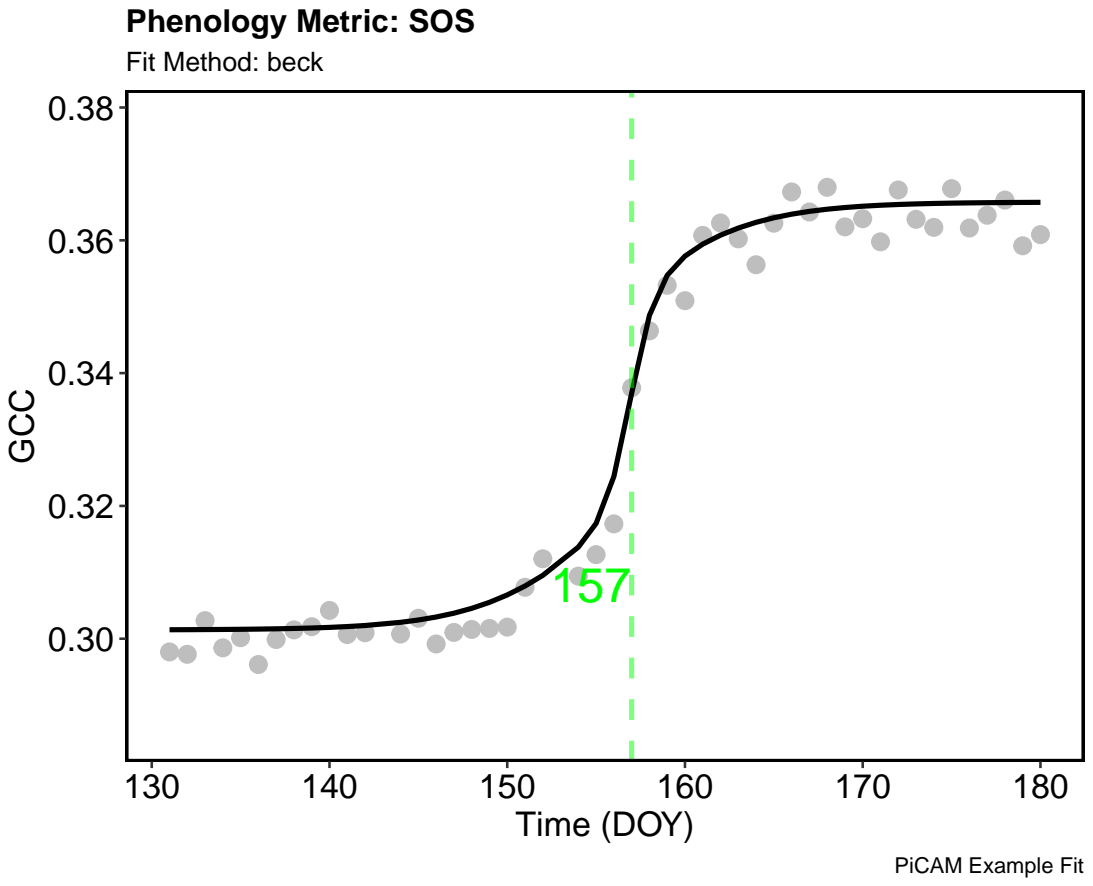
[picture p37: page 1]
Time (DOY); GCC

Phenology Metric: SOS
Fit Method: beck

PiCAM Example Fit

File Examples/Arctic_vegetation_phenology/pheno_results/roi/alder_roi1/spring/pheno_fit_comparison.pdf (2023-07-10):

0.011 | | pop | | pop eos | | | Senescence Maturity | | | SD | DD

## TRS

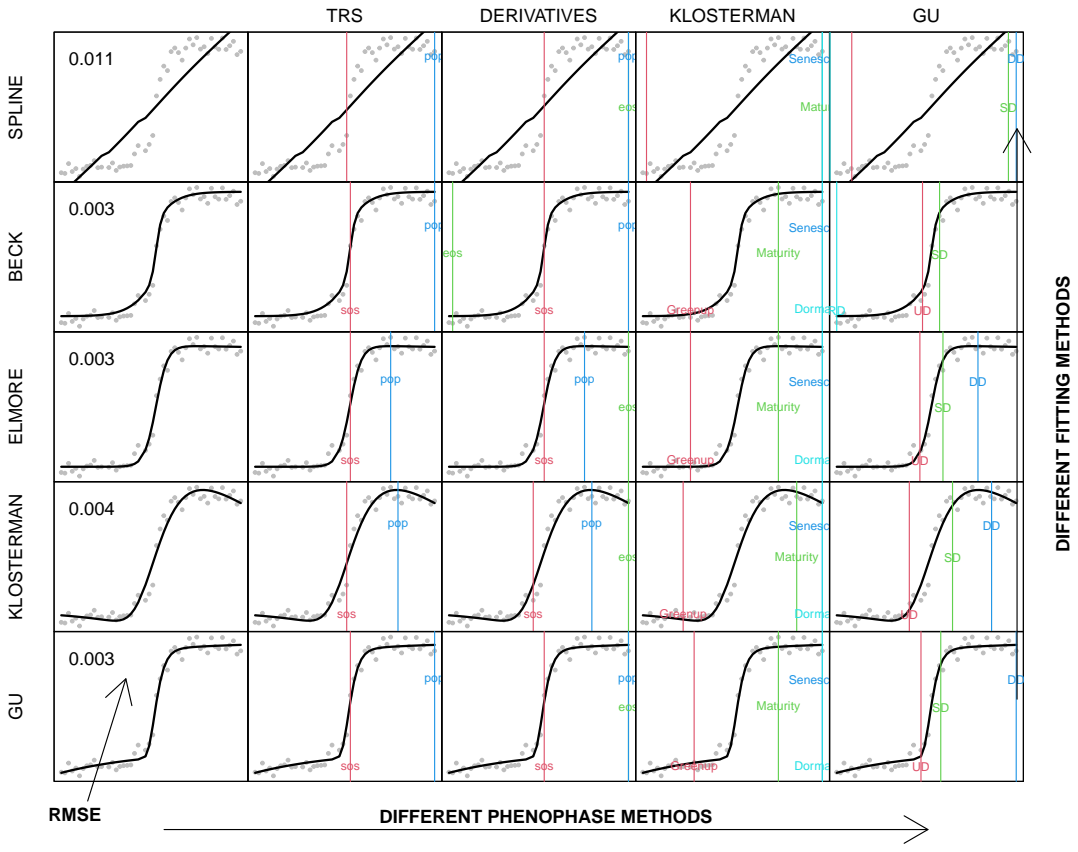
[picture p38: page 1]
x$data SPLINE; x$data; DERIVATIVES; KLOSTERMAN; BECK; ELMORE; x$data GU; RMSE

0.003 | sos | pop | eos | sos | pop | | Greenup | Maturity | Senescence Dormancy | | RD UD | SD

DIFFERENT FITTING METHODS

0.003 | sos | pop | sos | pop | eos | | Greenup | Maturity | Senescence Dormancy | | UD | SD | DD

0.004 | sos | pop | sos | pop | eos | | Greenup | Senescence Maturity | Dormancy | | UD | SD | DD

0.003 | sos | pop | sos | pop eos | | Greenup | Maturity | Senescence Dormancy | | UD | SD | DD

DIFFERENT PHENOPHASE METHODS

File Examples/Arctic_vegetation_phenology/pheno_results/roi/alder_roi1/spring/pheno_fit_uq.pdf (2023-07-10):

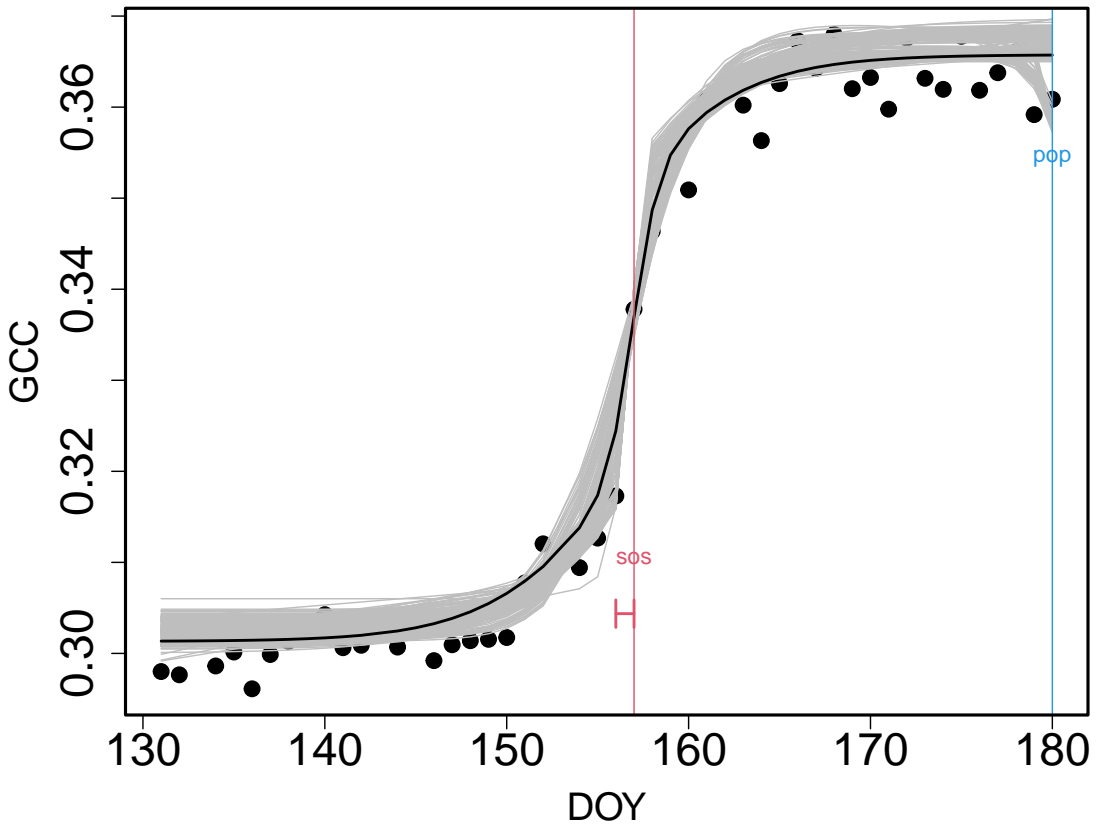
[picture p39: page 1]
DOY; GCC; sos; pop

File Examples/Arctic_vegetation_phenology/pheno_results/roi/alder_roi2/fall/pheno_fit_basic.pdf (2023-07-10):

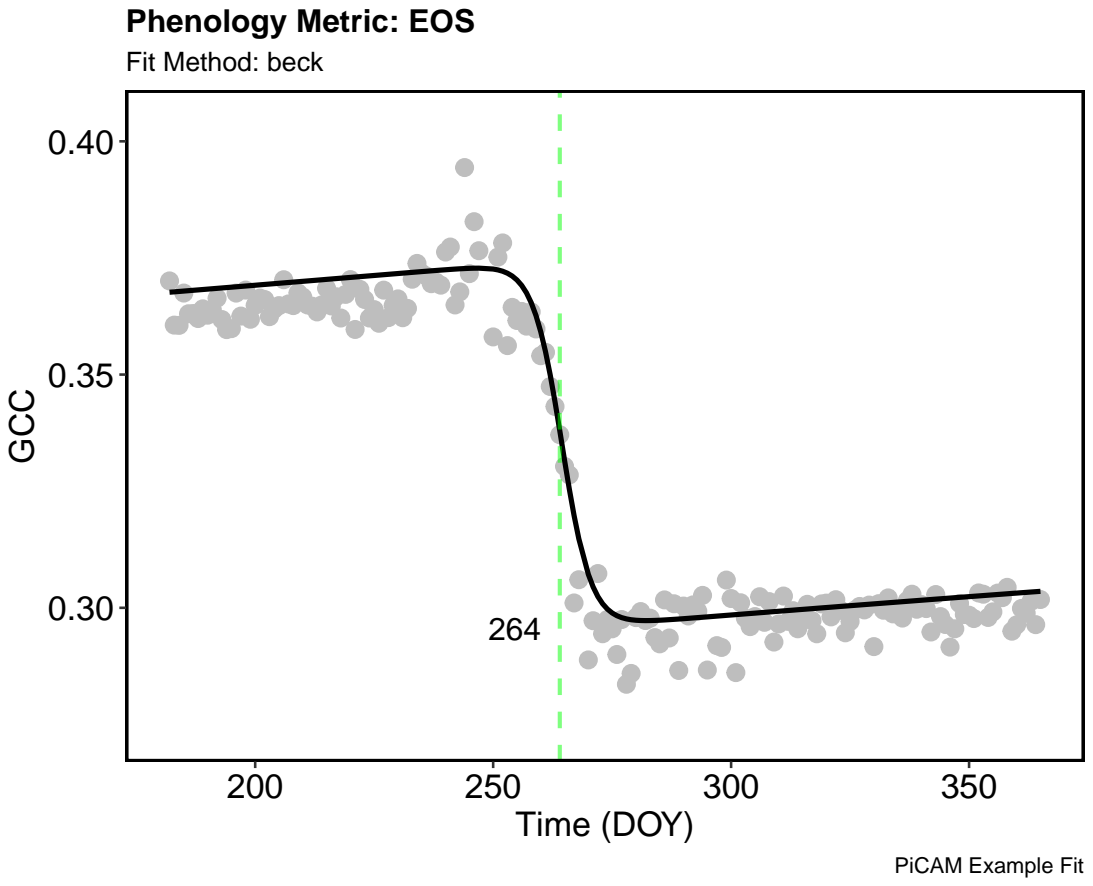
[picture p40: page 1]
Time (DOY); GCC

Phenology Metric: EOS
Fit Method: beck

PiCAM Example Fit

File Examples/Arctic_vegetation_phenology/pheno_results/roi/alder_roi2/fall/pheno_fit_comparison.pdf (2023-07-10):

0.006 | pop | eos | | sos | pop | eos | | Greenup | | Senescence Maturity | Dormancy | | SD | DD

## TRS

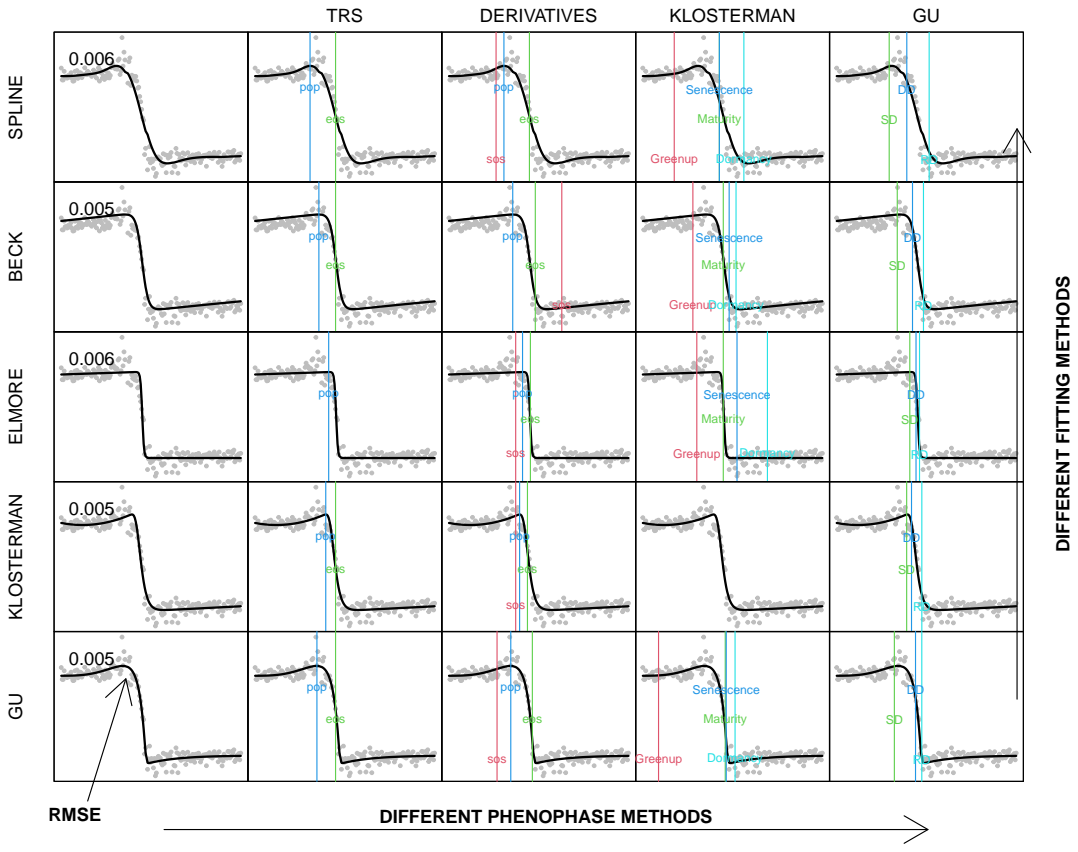
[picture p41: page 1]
x$data SPLINE; x$data; DERIVATIVES; KLOSTERMAN; BECK; ELMORE; x$data GU; RMSE

0.005 | pop | eos | | pop | eos | sos | | Greenup | Senescence Maturity Dormancy | | SD | DD | RD

DIFFERENT FITTING METHODS

0.006 | pop | | pop sos | | eos | | Greenup | Senescence Maturity | | Dormancy | | SD | DD RD

0.005 | pop | eos | | pop sos | eos | | | | DD SD | RD

0.005 | pop | eos | | sos | pop | eos | | | Greenup | Senescence Maturity Dormancy | | | SD | DD | RD

DIFFERENT PHENOPHASE METHODS

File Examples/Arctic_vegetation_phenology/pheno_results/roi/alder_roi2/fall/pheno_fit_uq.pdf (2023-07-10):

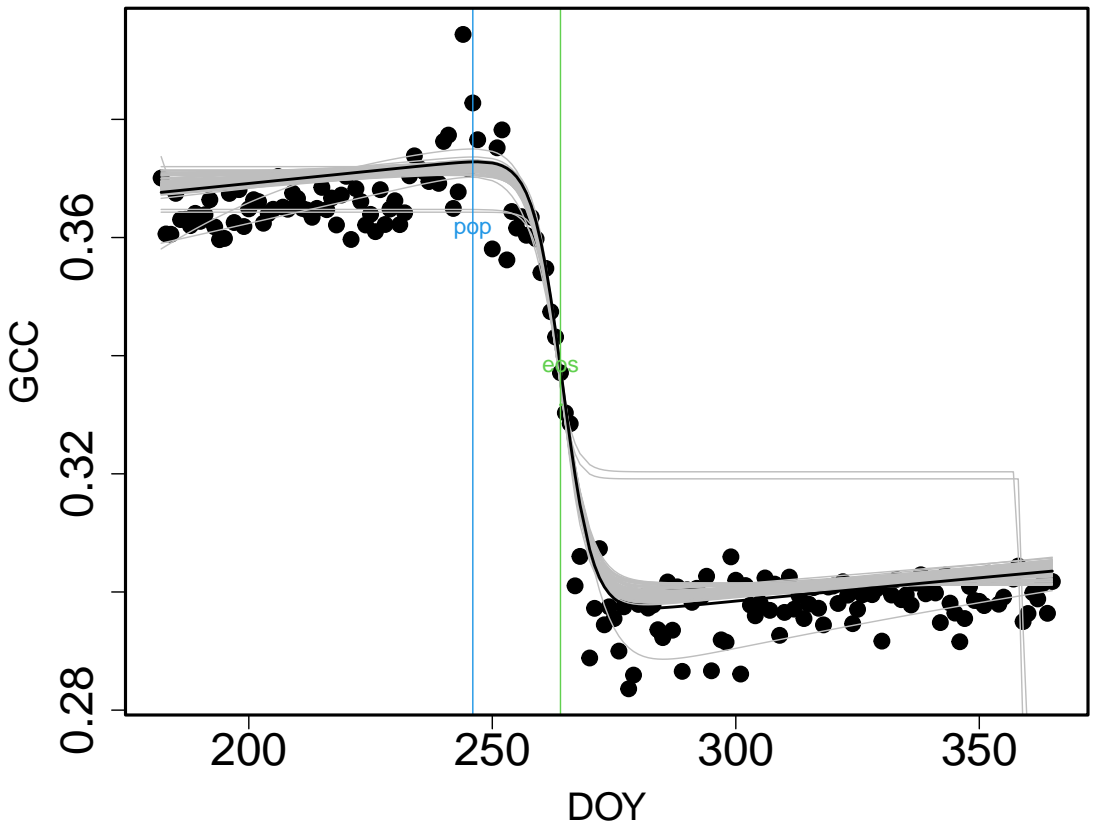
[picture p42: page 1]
DOY; GCC; eos; pop

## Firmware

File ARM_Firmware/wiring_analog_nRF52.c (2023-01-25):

/*
  Copyright (c) 2014 Arduino LLC.  All right reserved.
  Copyright (c) 2016 Sandeep Mistry All right reserved.

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
  You should have received a copy of the GNU Lesser General Public
  License along with this library; if not, write to the Free Software
  Foundation, Inc., 51 Franklin St, Fifth Floor, Boston, MA  02110-1301  USA
*/

#if defined(NRF52) || defined(NRF52_SERIES)

#include "nrf.h"

#include "Arduino.h"
#include "wiring_private.h"

#ifdef __cplusplus
extern "C" {
#endif

static uint32_t saadcReference = SAADC_CH_CONFIG_REFSEL_Internal;
static uint32_t saadcGain      = SAADC_CH_CONFIG_GAIN_Gain1_6;

static bool saadcBurst = SAADC_CH_CONFIG_BURST_Disabled;

// Note: Adafruit use seperated HardwarePWM class

static int readResolution = 10;
void analogReadResolution( int res )
{
  readResolution = res;
}

static inline uint32_t mapResolution( uint32_t value, uint32_t from, uint32_t to )
{
  if ( from == to )
  {
    return value ;
  }

  if ( from > to )
  {
    return value >> (from-to) ;
  }
  else
  {
    return value << (to-from) ;
  }
}

/*
 * Internal Reference is +/-0.6V, with an adjustable gain of 1/6, 1/5, 1/4,
 * 1/3, 1/2 or 1, meaning 3.6, 3.0, 2.4, 1.8, 1.2 or 0.6V for the ADC levels.
 *
 * External Reference is VDD/4, with an adjustable gain of 1, 2 or 4, meaning
 * VDD/4, VDD/2 or VDD for the ADC levels.
 *
 * Default settings are internal reference with 1/6 gain (GND..3.6V ADC range)
 *
 * Warning : On Arduino Zero board the input/output voltage for SAMD21G18 is 3.3 volts maximum
 */
void analogReference( eAnalogReference ulMode )
{
  switch ( ulMode ) {
    case AR_VDD4:
      saadcReference = SAADC_CH_CONFIG_REFSEL_VDD1_4;
      saadcGain      = SAADC_CH_CONFIG_GAIN_Gain1_4;
      break;
    case AR_INTERNAL_3_0:
      saadcReference = SAADC_CH_CONFIG_REFSEL_Internal;
      saadcGain      = SAADC_CH_CONFIG_GAIN_Gain1_5;
      break;
    case AR_INTERNAL_2_4:
      saadcReference = SAADC_CH_CONFIG_REFSEL_Internal;
      saadcGain      = SAADC_CH_CONFIG_GAIN_Gain1_4;
      break;
    case AR_INTERNAL_1_8:
      saadcReference = SAADC_CH_CONFIG_REFSEL_Internal;
      saadcGain      = SAADC_CH_CONFIG_GAIN_Gain1_3;
      break;
    case AR_INTERNAL_1_2:
      saadcReference = SAADC_CH_CONFIG_REFSEL_Internal;
      saadcGain      = SAADC_CH_CONFIG_GAIN_Gain1_2;
      break;
    case AR_DEFAULT:
    case AR_INTERNAL:
    default:
      saadcReference = SAADC_CH_CONFIG_REFSEL_Internal;
      saadcGain      = SAADC_CH_CONFIG_GAIN_Gain1_6;
      break;

  }
}

void analogOversampling( uint32_t ulOversampling )
{
	saadcBurst = SAADC_CH_CONFIG_BURST_Enabled;

	switch (ulOversampling) {
		case 0:
		case 1:
			saadcBurst = SAADC_CH_CONFIG_BURST_Disabled;
			NRF_SAADC->OVERSAMPLE = SAADC_OVERSAMPLE_OVERSAMPLE_Bypass;
			return;
			break;
		case 2:
			NRF_SAADC->OVERSAMPLE = SAADC_OVERSAMPLE_OVERSAMPLE_Over2x;
			break;
		case 4:
			NRF_SAADC->OVERSAMPLE = SAADC_OVERSAMPLE_OVERSAMPLE_Over4x;
			break;
		case 8:
			NRF_SAADC->OVERSAMPLE = SAADC_OVERSAMPLE_OVERSAMPLE_Over8x;
			break;
		case 16:
			NRF_SAADC->OVERSAMPLE = SAADC_OVERSAMPLE_OVERSAMPLE_Over16x;
			break;
		case 32:
			NRF_SAADC->OVERSAMPLE = SAADC_OVERSAMPLE_OVERSAMPLE_Over32x;
			break;
		case 64:
			NRF_SAADC->OVERSAMPLE = SAADC_OVERSAMPLE_OVERSAMPLE_Over64x;
			break;
		case 128:
			NRF_SAADC->OVERSAMPLE = SAADC_OVERSAMPLE_OVERSAMPLE_Over128x;
			break;
		case 256:
			NRF_SAADC->OVERSAMPLE = SAADC_OVERSAMPLE_OVERSAMPLE_Over256x;
			break;
	}
}

static uint32_t analogRead_internal( uint32_t psel )
{
  uint32_t saadcResolution;
  uint32_t resolution;
  volatile int16_t value = 0;

  if (readResolution <= 8) {
    resolution = 8;
    saadcResolution = SAADC_RESOLUTION_VAL_8bit;
  } else if (readResolution <= 10) {
    resolution = 10;
    saadcResolution = SAADC_RESOLUTION_VAL_10bit;
  } else if (readResolution <= 12) {
    resolution = 12;
    saadcResolution = SAADC_RESOLUTION_VAL_12bit;
  } else {
    resolution = 14;
    saadcResolution = SAADC_RESOLUTION_VAL_14bit;
  }

  NRF_SAADC->RESOLUTION = saadcResolution;

  NRF_SAADC->ENABLE = (SAADC_ENABLE_ENABLE_Enabled << SAADC_ENABLE_ENABLE_Pos);
  for (int i = 0; i < 8; i++) {
    NRF_SAADC->CH[i].PSELN = SAADC_CH_PSELP_PSELP_NC;
    NRF_SAADC->CH[i].PSELP = SAADC_CH_PSELP_PSELP_NC;
  }
  NRF_SAADC->CH[0].CONFIG = ((SAADC_CH_CONFIG_RESP_Bypass     << SAADC_CH_CONFIG_RESP_Pos)   & SAADC_CH_CONFIG_RESP_Msk)
                            | ((SAADC_CH_CONFIG_RESP_Bypass   << SAADC_CH_CONFIG_RESN_Pos)   & SAADC_CH_CONFIG_RESN_Msk)
                            | ((saadcGain                     << SAADC_CH_CONFIG_GAIN_Pos)   & SAADC_CH_CONFIG_GAIN_Msk)
                            | ((saadcReference                << SAADC_CH_CONFIG_REFSEL_Pos) & SAADC_CH_CONFIG_REFSEL_Msk)
                            | ((SAADC_CH_CONFIG_TACQ_3us      << SAADC_CH_CONFIG_TACQ_Pos)   & SAADC_CH_CONFIG_TACQ_Msk)
                            | ((SAADC_CH_CONFIG_MODE_SE       << SAADC_CH_CONFIG_MODE_Pos)   & SAADC_CH_CONFIG_MODE_Msk)
                            | ((saadcBurst                    << SAADC_CH_CONFIG_BURST_Pos)   & SAADC_CH_CONFIG_BURST_Msk);
  NRF_SAADC->CH[0].PSELN = psel;
  NRF_SAADC->CH[0].PSELP = psel;


  NRF_SAADC->RESULT.PTR = (uint32_t)&value;
  NRF_SAADC->RESULT.MAXCNT = 1; // One sample

  NRF_SAADC->TASKS_START = 0x01UL;

  while (!NRF_SAADC->EVENTS_STARTED);
  NRF_SAADC->EVENTS_STARTED = 0x00UL;

  NRF_SAADC->TASKS_SAMPLE = 0x01UL;

  while (!NRF_SAADC->EVENTS_END);
  NRF_SAADC->EVENTS_END = 0x00UL;

  NRF_SAADC->TASKS_STOP = 0x01UL;

  while (!NRF_SAADC->EVENTS_STOPPED);
  NRF_SAADC->EVENTS_STOPPED = 0x00UL;

  if (value < 0) {
    value = 0;
  }

  NRF_SAADC->ENABLE = (SAADC_ENABLE_ENABLE_Disabled << SAADC_ENABLE_ENABLE_Pos);

  return mapResolution(value, resolution, readResolution);
}


uint32_t analogRead( uint32_t ulPin )
{
  uint32_t psel = SAADC_CH_PSELP_PSELP_NC;

  if (ulPin >= PINS_COUNT) {
    return 0;
  }

  ulPin = g_ADigitalPinMap[ulPin];

  switch ( ulPin ) {
    case 2:
      psel = SAADC_CH_PSELP_PSELP_AnalogInput0;
      break;

    case 3:
      psel = SAADC_CH_PSELP_PSELP_AnalogInput1;
      break;

    case 4:
      psel = SAADC_CH_PSELP_PSELP_AnalogInput2;
      break;

    case 5:
      psel = SAADC_CH_PSELP_PSELP_AnalogInput3;
      break;

    case 28:
      psel = SAADC_CH_PSELP_PSELP_AnalogInput4;
      break;

    case 29:
      psel = SAADC_CH_PSELP_PSELP_AnalogInput5;
      break;

    case 30:
      psel = SAADC_CH_PSELP_PSELP_AnalogInput6;
      break;

    case 31:
      psel = SAADC_CH_PSELP_PSELP_AnalogInput7;
      break;

    default:
      return 0;
  }

  return analogRead_internal(psel);
}

uint32_t analogReadVDD( void )
{
  return analogRead_internal(SAADC_CH_PSELP_PSELP_VDD);
}

uint32_t analogReadVDDHDIV5( void )
{
  return analogRead_internal(SAADC_CH_PSELP_PSELP_VDDHDIV5);
}

#ifdef __cplusplus
}
#endif

#endif

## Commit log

2023-01-25 Adds files and license info
    [D-cell_Pi_Side_v11.stl, D-cell_nrf_Side_v11.stl, cam_gps_holder_v2c.stl, cam_holder_v2c.FCStd]
2023-07-04 Cleanup and re-org. Added Examples/install_dependencies.R
    [PiCam_014_20210820_20220724_roi1.csv, PiCam_014_20210820_20220724_roi2.csv, PiCam_014_20210820_20220724_roi3.csv, PiCam_014_20210820_20220724_roi4.csv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]
2023-07-05 Updating the examples. Working on a image extract function before updating the phenofitting codes
    [PiCam_014_20210820_20220724_roi1.csv, PiCam_014_20210820_20220724_roi2.csv, PiCam_014_20210820_20220724_roi3.csv, PiCam_014_20210820_20220724_roi4.csv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]
2023-07-07 Updates. removed data from the git repo and replaced with an archive on OSF.io. Additional updates to create the example code in full R
    [log.csv]
2023-07-09 Removed the old results based on the older IDL and R code
    [PiCam_014_20210820_20220724_roi1.csv, PiCam_014_20210820_20220724_roi2.csv, PiCam_014_20210820_20220724_roi3.csv, PiCam_014_20210820_20220724_roi4.csv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]
